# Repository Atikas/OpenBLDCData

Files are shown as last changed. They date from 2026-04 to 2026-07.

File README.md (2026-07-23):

# Open BLDC Motor Test-Bench Dataset for Vibration and Current Analysis

## Introduction

### Motivation and Scope

This dataset is intended to support research and engineering work on practical
condition monitoring of BLDC motor systems. BLDC motors are widely used in
automation, robotics, ventilation, pumps, electric mobility, and other compact
electromechanical systems, but openly available BLDC datasets with synchronized
vibration, current, speed-related pulse information, and documented operating
conditions remain limited. This repository is created to reduce that gap by
providing raw measurements collected from a transparent and reproducible
test-bench arrangement.

The test bench used to collect the recordings is shown below.

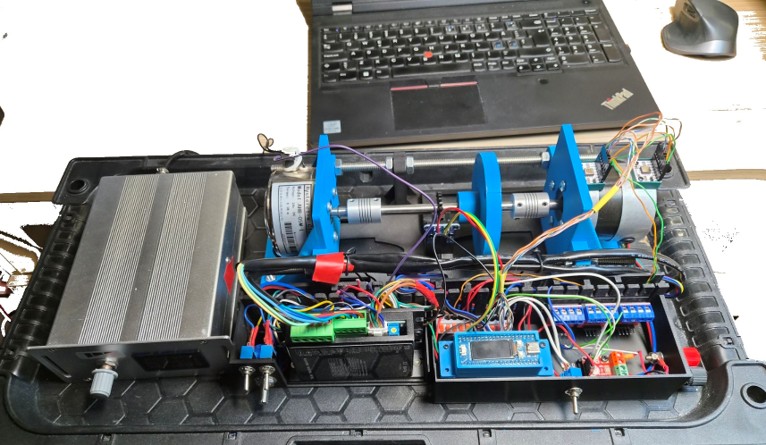
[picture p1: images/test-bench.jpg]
Test bench


A central idea of this dataset is that the measurement chain is based on a
low-cost and low-power acquisition device rather than on laboratory-grade
industrial instrumentation only. The use of an RP2350-based microcontroller, ADXL355
accelerometers, and INA226 electrical sensing reflects the type of hardware that
can plausibly be embedded near real machines, deployed in multiple locations,
or used in cost-sensitive industrial monitoring systems. This is important
because many condition-monitoring methods work well under ideal laboratory
conditions but become difficult to transfer when the sensing platform is too
expensive, power-hungry, or impractical for distributed use.

The recordings are therefore aimed at realistic algorithm development: signal
processing, feature extraction, anomaly detection, fault classification, sensor
fusion, robustness testing, and evaluation of models under non-ideal acquisition
conditions. The presence of sampling-time jitter, different motor loads,
different speed regimes, alternative power sources, a baseline noise recording,
and environmentally contaminated `ENV` recordings makes the dataset useful for
studying not only clean fault signatures, but also the measurement artifacts and
disturbances that appear in practical deployments.

Potential uses of the dataset include:

- Multimodal fault diagnosis using vibration, current, and rotational-speed data.
- Anomaly detection and self-supervised representation learning with limited labels.
- Domain adaptation across motor units, speeds, loads, power sources, and environmental conditions.
- Calibration and validation of physics-based models and digital twins.
- Signal reconstruction, denoising, missing-sample recovery, and sampling-jitter compensation.
- Virtual sensing of speed, load, or machine condition from a reduced set of measured channels.
- Development of edge condition-monitoring methods for resource-constrained acquisition hardware.
- Reproducible laboratory exercises in signal processing, machine diagnostics, and condition monitoring.

### Data Acquisition Components

This section describes the microcontroller and sensors used to collect vibration and electrical measurements, together with their connections in the test bench.

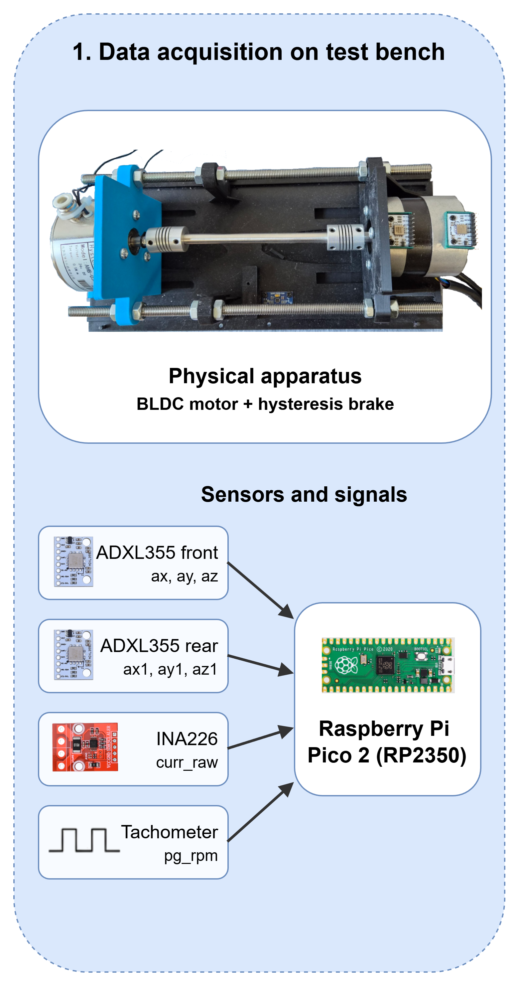
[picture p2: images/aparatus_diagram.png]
Data-acquisition component diagram


#### Microcontroller

Data acquisition was performed using a [Waveshare RP2350-LCD-0.96](https://www.waveshare.com/rp2350-lcd-0.96.htm), a Pico-compatible board based on the Raspberry Pi RP2350A. It has a 0.96-inch 160 × 80 IPS LCD, 26 GPIO pins, and SPI, I²C, UART, and 12-bit ADC interfaces for the test-bench sensors. The LCD was not needed for data acquisition, but it was useful during setup and experiments. The device produces a small sampling-time jitter. See [`sampling_validation.ipynb`](src/sampling_validation.ipynb) for a detailed validation of the sampling intervals.

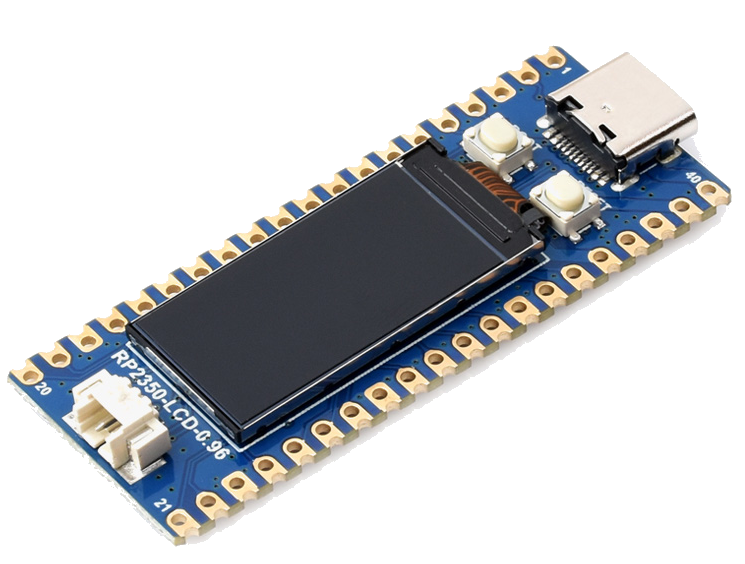
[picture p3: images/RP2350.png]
Waveshare RP2350-LCD-0.96 data-acquisition device


#### ADXL355 Accelerometers

Vibration was measured with two [ADXL355](<adxl354_adxl355.pdf>) three-axis MEMS accelerometers. One sensor was mounted on the front bearing ring and the other on the rear bearing ring. Both sensors were connected to the RP2350 through SPI. 

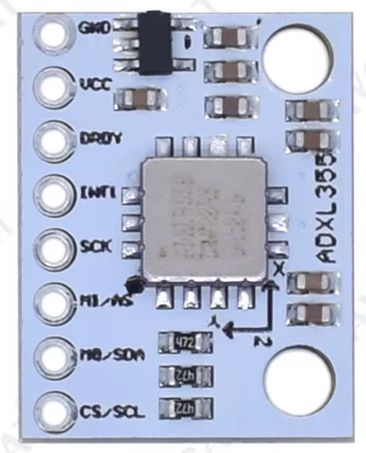
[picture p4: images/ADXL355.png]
ADXL355 accelerometer


The active firmware settings and key ADXL355 characteristics from the [ADXL354/ADXL355 data sheet](<adxl354_adxl355.pdf>) are listed below.

| Parameter | Value | Source |
| --- | --- | --- |
| Measurement range | ±4 g | Firmware setting |
| Output data rate | 2 kHz | Firmware setting |
| Low-pass filter corner frequency | 500 Hz | Firmware setting |
| High-pass filter | Disabled | Firmware setting |
| Acceleration output | 20-bit signed raw values | Firmware setting |
| Sensor mode | Measurement mode | Firmware setting |
| SPI bus | 4-wire SPI, Mode 0, 600 kHz | Firmware setting |
| SPI chip-select pins | GPIO 17 for one sensor and GPIO 20 for the other | Firmware setting |
| Data-ready handling | `DATA_RDY` status bit is polled with an 800 µs timeout | Firmware setting |
| Sensitivity at the configured ±4 g range | 128,000 LSB/g typical, or 7.8 µg/LSB | Data sheet |
| ADC resolution | 20 bits | Data sheet |
| Noise spectral density | 22.5 µg/√Hz at ±2 g; 25 µg/√Hz at ±8 g. The data sheet does not specify a separate typical value for ±4 g. | Data sheet |
| 0 g offset drift over temperature | 0.15 mg/°C maximum | Data sheet |
| Cross-axis sensitivity | 1% | Data sheet |
| Operating temperature range | −40°C to +125°C | Data sheet |
| Typical current in measurement mode | 200 µA with the internal LDO enabled | Data sheet |

#### INA226 Current Sensor

Electrical measurements were made with an INA226 current and power monitor placed before the BLDC motor driver. It records the shunt voltage, bus voltage, and current. The INA226 is connected to the RP2350 through I²C0 at address `0x40` and a bus speed of 400 kHz.

| Parameter | Set value |
| --- | --- |
| Shunt resistor | 2 mΩ (`R002`) |
| Maximum expected current | 10 A |
| Current scale | 305.18 µA/LSB |
| Averaging | 1 sample |
| Bus-voltage conversion time | 588 µs |
| Shunt-voltage conversion time | 588 µs |
| Operating mode | Continuous shunt- and bus-voltage conversion |

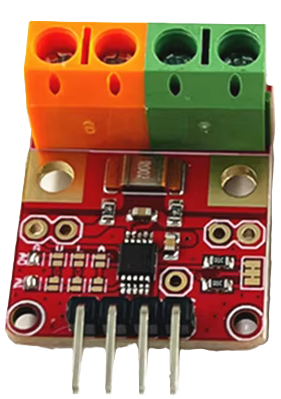
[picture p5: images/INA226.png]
INA226 current sensor


#### UM34C USB Power Meter

The RP2350 acquisition device was powered from a laptop USB port, and its
current was measured with a UM34C USB power meter. The measured current was
approximately 0.034 A during this test. This value should be treated as
indicative rather than fully representative because the microcontroller LCD was
enabled during the measurement. Measurements with the LCD disabled and firmware
optimized for current measurement are WIP.

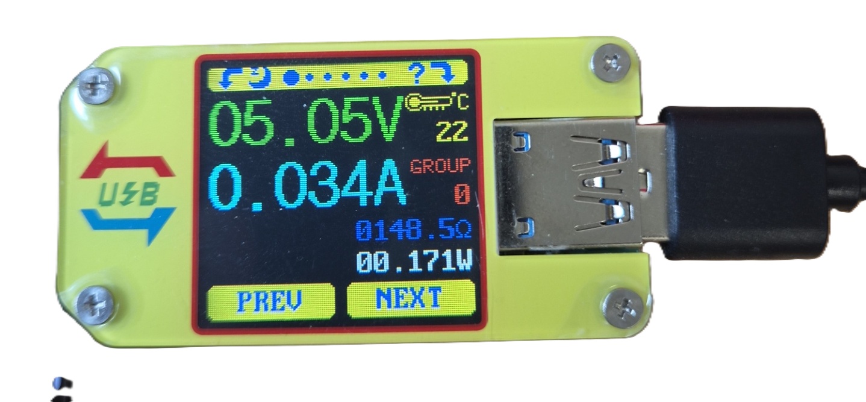
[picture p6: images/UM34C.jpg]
RP2350 current measurement with UM34C


### 3D-Printed Construction Parts

The `3d_prints/` directory contains the STL files used to 3D print the test-bench
mounts and other mechanical parts. The files can be used to reproduce or modify
the mechanical setup shown in the test-bench image above and should be used with
the hardware components listed below. The parts in the current test bench were
printed from PLA.

### Hardware Components

The main hardware components are:

| Component | Model / description |
| --- | --- |
| Motor driver | [BD10LR BLDC](<BLD-120A updated(BD10LR).pdf>) |
| Motor under test (MUT) | [STEPPEROLINE BLDC Motor 57BYA54-24-01](<57BYA54-24-01.pdf>) |
| Load | Hysteresis Brake AHB-05M |
| Battery supply | NP-12-1.2Ah lead-acid battery, 2x in series |
| Laboratory power supply | UNIT-T UTP3305 |

### MUT Parameters

The motor under test is a BLDC Motor 57BYA54-24-01 with the following nominal
parameters:

| Parameter | Value |
| --- | --- |
| Phase | 3 |
| Poles | 4 |
| Rated voltage | 24 V |
| Rated torque | 0.16 Nm (22.66 oz.in) |
| Rated power | 50 W |
| Rated speed | 3000 +/- 10% rpm |
| Rated current | 2.90 A |
| No-load speed | 3800 +/- 10% rpm |
| Resistance per phase | 1.02 +/- 10% Ohms |
| Inductance per phase | 2.61 +/- 20% mH |

### Faults

#### Front bearing fault

The front bearing is a 608ZZ (8 × 22 × 7 mm) deep-groove ball bearing. A rolling-element fault was introduced by grinding the surface of one of the seven 3.969 mm balls. This produces repeated impacts at twice the ball-spin frequency (2 × BSF). Fault validation is documented in [`src/bearing_fault_validation.ipynb`](src/bearing_fault_validation.ipynb).

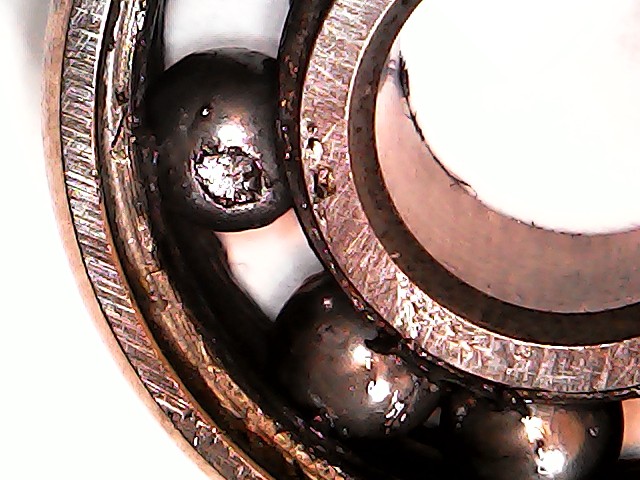
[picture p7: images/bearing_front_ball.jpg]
Front bearing 608ZZ — ball defect


An outer-race fault condition is also being prepared (WIP).

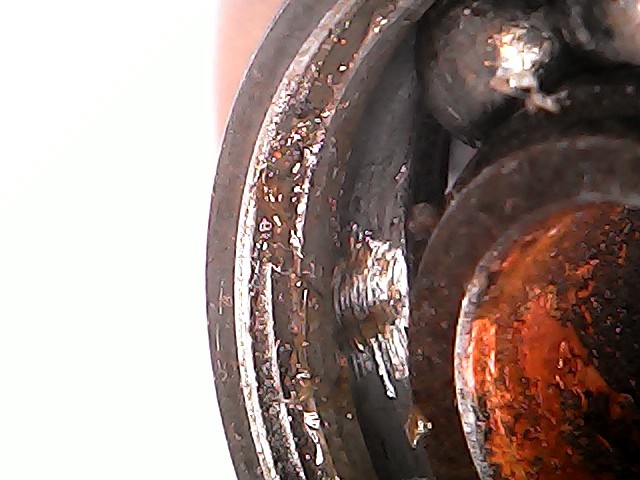
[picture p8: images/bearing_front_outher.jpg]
Front bearing 608ZZ — outer race


#### Rear bearing fault

The rear bearing is a 606ZZ (6 × 17 × 6 mm) deep-groove ball bearing. A rolling-element fault was introduced by grinding the surface of one of the balls.

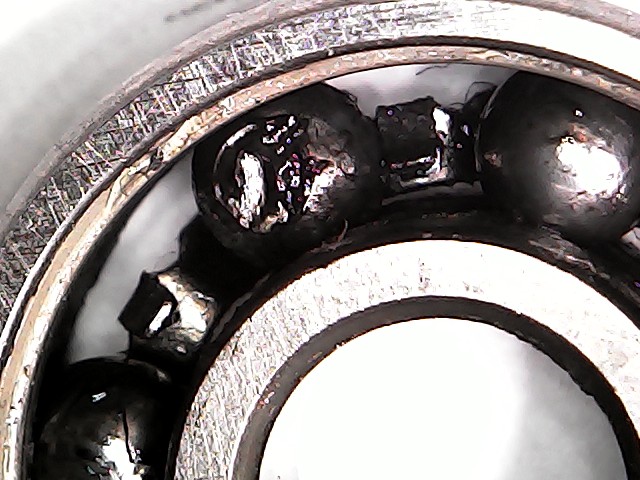
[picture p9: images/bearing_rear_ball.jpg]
Rear bearing 606ZZ — ball defect


#### Shaft misalignment

The shaft misalignment fault was introduced by setting a 2.5° angular
offset between the motor shaft and the coupled load shaft. 

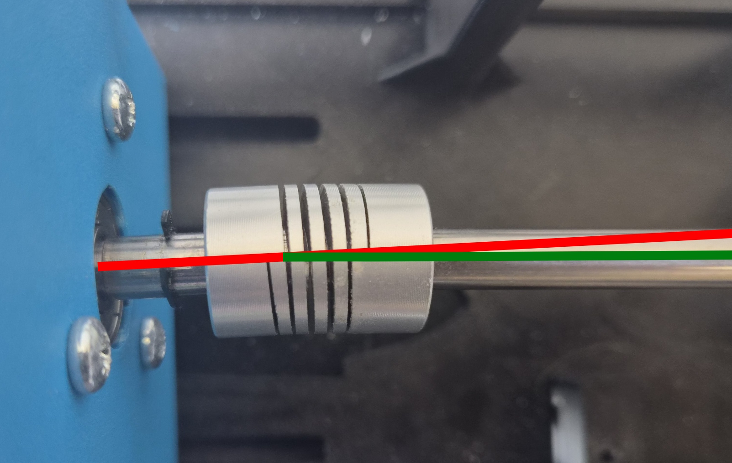
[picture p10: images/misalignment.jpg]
Shaft misalignment


### Data Files

CSV files are stored in the `data/` directory.

Most file names follow this structure:

```text
analize_<state><id>[_quality]_<speed>rpm_<load-current>mA_<power-source>.csv
```

Example:

```text
analize_healthy16_ENV_1000rpm_64mA_bat.csv
```

The `<state>` field identifies the MUT health state. The dataset covers the
following MUT health states. Per-state file counts and sizes are available in
[`src/data_summary.ipynb`](src/data_summary.ipynb).

| State | Status | Description |
| --- | --- | --- |
| healthy | 100% | Reference operating condition without the faults. |
| front_ball | 100% | Fault condition associated with the front bearing. |
| rear_ball | 100% | Fault condition associated with the rear bearing. |
| misalignment | 100% | Fault condition associated with shaft misalignment. |
| demag | WIP | Fault condition associated with weakened motor magnets. |

The number `<id>` immediately following the `<state>` label encodes both the 
motor unit and the experiment number.
The first digit(s) indicate the motor unit, and the last digit indicates the
experiment number with same conditions. For example, `10` means motor 2, 
experiment 1; `25` means motor 3, experiment 6. The fault conditions were kept 
identical across motor units `1`, `2`, and `3`.
The same faulty 608ZZ front bearing, the same faulty 606ZZ rear bearing, and the
same 2.5° angular misalignment setup were used for each motor.
Motor index `0` is reserved exclusively for demagnetisation experiments and is 
not used for any other state.

The `<speed>rpm` field indicates the approximate MUT speed setpoint. The
main dataset covers operating speeds of 500, 1000, and 1500 rpm. Additional
recordings at 2000, 2500, and 3000 rpm are provided as supplementary data and
are limited to 75% or 100% motor load. The exact rotational speed can be
calculated from the `pg_rpm` pulse signal, where six pulses correspond to one
full mechanical revolution. A Python example of this calculation is provided in
[`src/RPM_calculation.ipynb`](src/RPM_calculation.ipynb).

The `<load-current>mA` field indicates the current setting used to define the
approximate mechanical load. The mapping is given below.
The current value in each file name corresponds to the approximate motor load:

| Motor load | Current |
| --- | --- |
| ~15% | 19 mA |
| ~30% | 38 mA |
| ~50% | 64 mA |
| ~75% | 96 mA |
| ~100% | 128 mA |

The `<power-source>` suffix identifies the motor power source:

| Suffix | Motor power source |
| --- | --- |
| `bat` | Two NP-12-1.2Ah lead-acid batteries connected in series. |
| `mait` | UNIT-T UTP3305 laboratory power supply. |

## Optional Quality Parameter

The `[_quality]` part of the file-name structure is an optional parameter that
describes signal quality. 

| `<quality>` value | Meaning | Description |
| --- | --- | --- |
| `ENV` | Environmental contamination | The recording contains environmental disturbances, such as footsteps, wind, nearby transport, or structural vibrations transmitted through the surroundings. |
| `SF` | Sensor failure or drift | The recording is affected by a sensor failure or sensor drift. |
| No label | Clean signal | No significant environmental contamination, sensor failure, or sensor drift was identified in the recording. |

## Baseline

The dataset also includes a baseline recording, `data/analize_0rpm_0mA.csv`,
captured with the test bench switched off. This file represents the background
sensor noise of the measurement chain without motor rotation or load current.

## CSV Columns

Each CSV file uses the following columns:

| Column | Description |
| --- | --- |
| `t_us` | Sample timestamp in microseconds. |
| `ax`, `ay`, `az` | ADXL355 vibration sensor axes measured on the front bearing ring, bearing type 608ZZ 8x22x7. |
| `ax1`, `ay1`, `az1` | ADXL355 vibration sensor axes measured on the rear bearing ring, bearing type 606ZZ 6x17x6. |
| `shunt_raw` | Raw INA226 shunt-voltage reading from the current sensor placed before the BLDC motor driver. |
| `bus_raw` | Raw INA226 bus-voltage reading from the current sensor placed before the BLDC motor driver. |
| `curr_raw` | Raw INA226 current reading from the current sensor placed before the BLDC motor driver. |
| `pg_rpm` | Square-wave pulse signal from the BLD10LR motor driver PG (pulse generator) output, used as a tachometer signal. Logic levels: 0/1. Six pulses correspond to one full mechanical revolution. |
| `seq` | Sample sequence counter. |
| `dt` | Time difference between samples; use this together with `t_us` to account for the small sampling-time jitter. |

## License

The data and documentation in this repository are licensed under the Creative
Commons Attribution 4.0 International License (CC BY 4.0).
Full license text: https://creativecommons.org/licenses/by/4.0/legalcode.

You may use, copy, distribute, and adapt the data only if you give appropriate
credit to the author.

Recommended citation:

> Robertas Ūselis. Open BLDC Motor Test-Bench Dataset for Vibration and Current Analysis. 2026. https://github.com/Atikas/OpenBLDCData.
> License: CC BY 4.0.

If you modify the data, indicate that changes were made.

## FAIR Principles

This dataset is designed to align with the [FAIR data principles](https://www.go-fair.org/fair-principles/) (Findable, Accessible, Interoperable, Reusable):

| Principle | How it is addressed |
| --- | --- |
| **Findable** | The dataset is publicly hosted on GitHub at https://github.com/Atikas/OpenBLDCData. File names encode experimental conditions, making individual recordings easy to identify without opening the files. |
| **Accessible** | All data files are openly available without authentication. The repository can be cloned or individual files downloaded directly via standard HTTPS. |
| **Interoperable** | Data is stored in plain CSV format with clearly named columns and explicit timestamp information. No proprietary software or format is required to read the files. |
| **Reusable** | Each file is accompanied by a documented measurement setup, hardware description, column definitions, and operating conditions in this README. The dataset is released under CC BY 4.0, which permits broad reuse with attribution. |

<!-- > **Note:** A persistent identifier (DOI) has not yet been assigned. For long-term citability and formal publication, archiving the dataset on a repository such as [Zenodo](https://zenodo.org) is recommended. -->

## Collaboration

If your research requires operating conditions or measurements that are not
currently included in the dataset, please open a GitHub issue describing the
data you need. I am open to collaboration and may be able to collect additional
measurements using this test bench.

<!-- ## Support

If you find this dataset useful, you can support my work through
[Buy Me a Coffee](https://buymeacoffee.com/atikas).

[![Buy Me a Coffee QR code](images/buymeacoffe-code.png)](https://buymeacoffee.com/atikas) -->

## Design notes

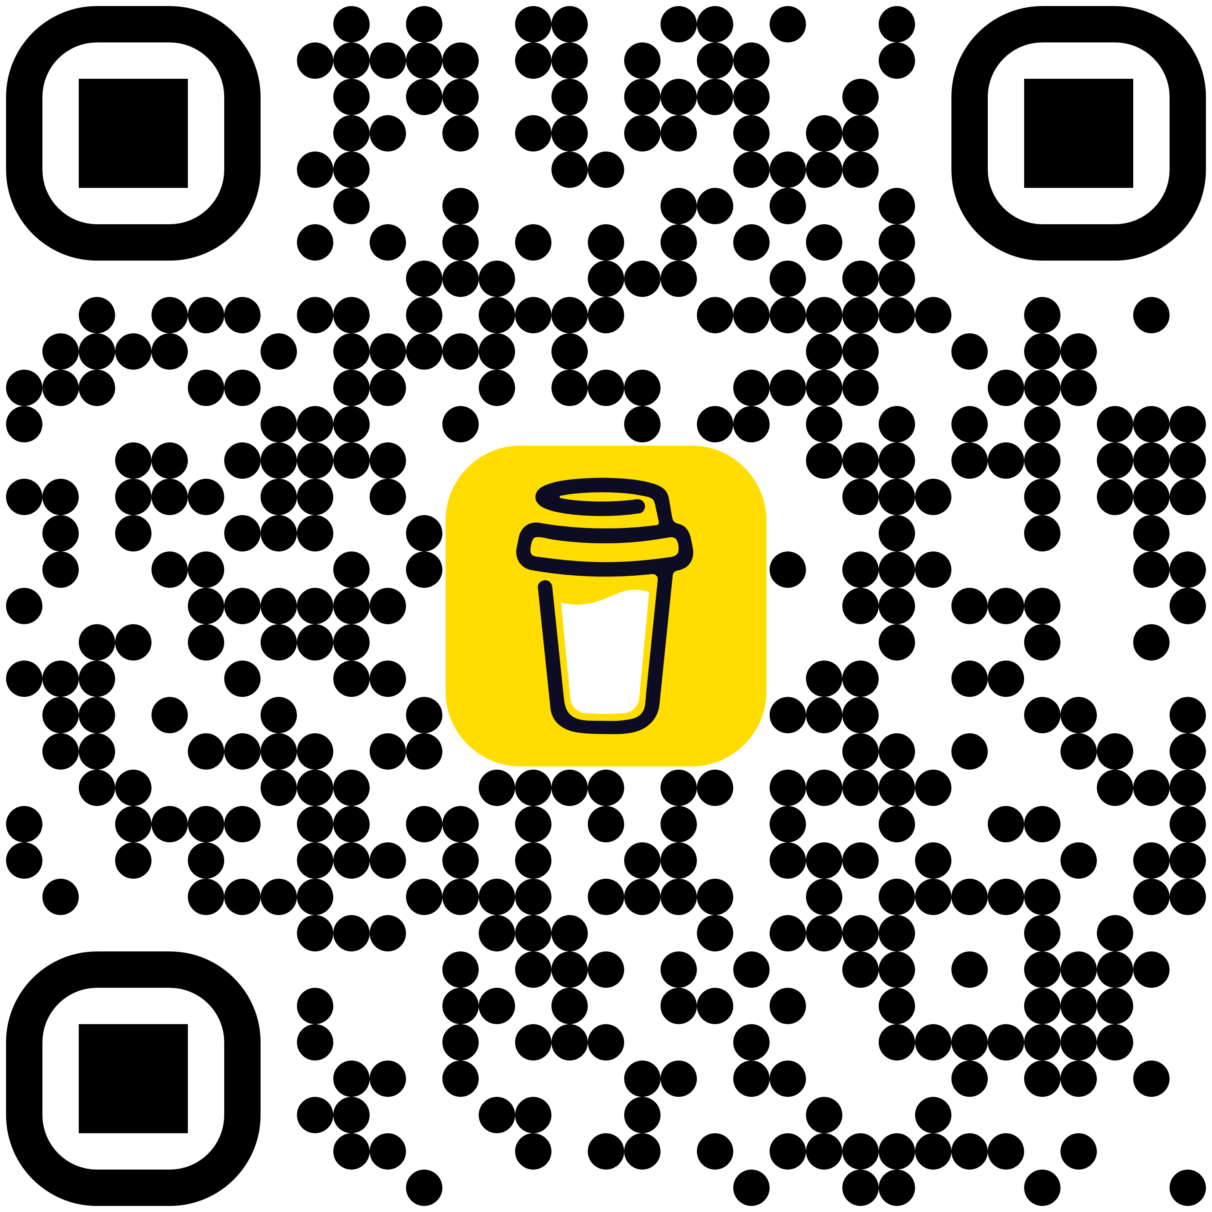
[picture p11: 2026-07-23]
images/buymeacoffe-code.png

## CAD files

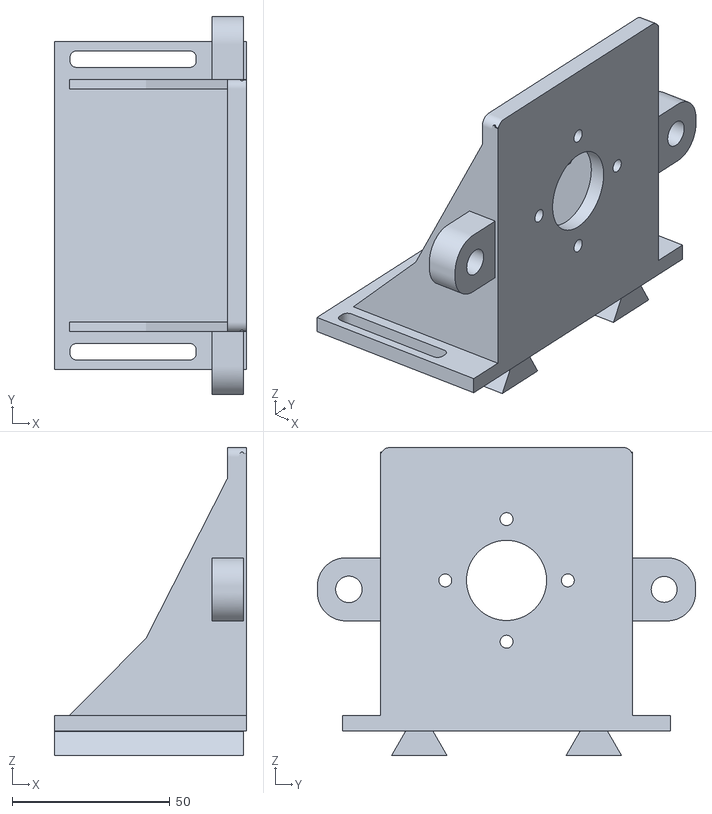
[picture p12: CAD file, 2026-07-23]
3d_prints/MUT-L-bracket.stl
61.0 x 120.0 x 97.7

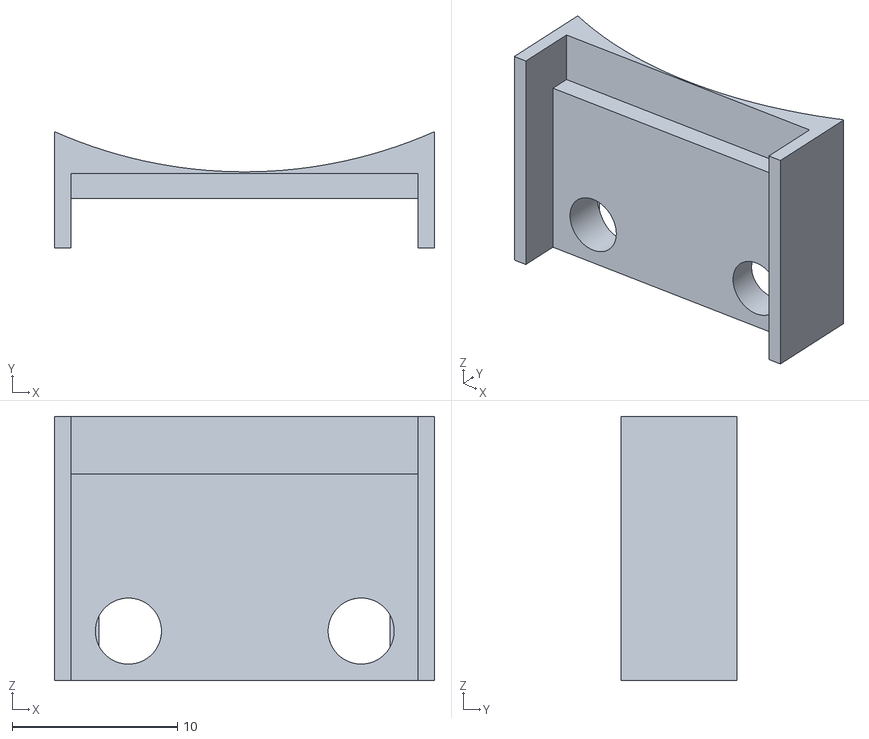
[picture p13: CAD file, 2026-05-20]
3d_prints/sensor-adapter.stl
23.0 x 7.00 x 16.0

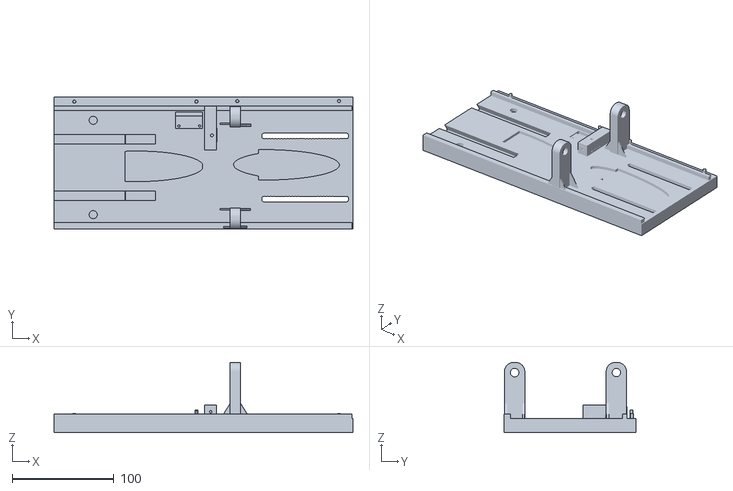
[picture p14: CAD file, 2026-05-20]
3d_prints/aparatus-bottom.stl
294.0 x 129.8 x 69.0

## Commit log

2026-04-26 more Healthy data
    [analize_healthy16_ENV_1000rpm_64mA_bat.csv]
2026-04-26 more data
    [analize_healthy16_ENV_1000rpm_64mA_bat.csv]
2026-04-26 ENV 1000
    [analize_healthy16_ENV_1000rpm_64mA_bat.csv]
2026-05-20 sensor adapter
    [sensor-adapter.stl]
2026-05-21 d3 prints
    [aparatus-bottom.stl, sensor-adapter.stl]
